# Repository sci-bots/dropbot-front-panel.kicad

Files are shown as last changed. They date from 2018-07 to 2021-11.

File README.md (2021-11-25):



# DropBot v3 front panel

The front panel board provides the power (+3.3V, +12V) and communication (i2c) bus for the other boards in the [DropBot v3 system][dropbot] and routes the high-voltage outputs from the switching boards to the pogo-pin board.

For more information, please visit https://sci-bots.com

[Sci-Bots logo][sci-bots]

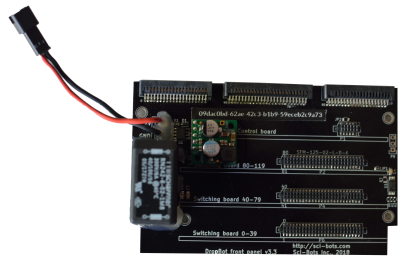
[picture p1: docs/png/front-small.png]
front

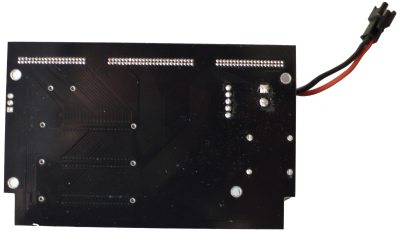
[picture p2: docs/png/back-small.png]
back


This design is open-source hardware released under a [Creative Commons Attribution-ShareAlike licence][cc-by-sa].

[][cc-by-sa]

[dropbot]: https://github.com/sci-bots/dropbot-v3
[sci-bots]: https://sci-bots.com/
[cc-by-sa]: http://creativecommons.org/licenses/by-sa/3.0

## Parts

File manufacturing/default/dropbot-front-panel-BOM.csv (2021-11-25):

Refs | Quantity | MPN | Manufacturer | datasheet | footprint | value
C1-C4 | 4 | CL21B104KBCNNNC | Samsung |  | Capacitors_SMD:C_0805 | 0.1uF
D1 | 1 | MMSZ5240BS-7-F | Diodes Inc. |  | Diodes_SMD:D_SOD-323 | 10V
JP1 | 1 | RC0805JR-070RL | Yageo |  | Resistors_SMD:R_0805 | JUMPER
JP2 | 1 | DNP | DNP |  | Resistors_SMD:R_0805 | JUMPER
JP3 | 1 | DNP | DNP |  | Resistors_SMD:R_0603 | A0
JP4 | 1 | DNP | DNP |  | Resistors_SMD:R_0603 | A1
JP5 | 1 | DNP | DNP |  | Resistors_SMD:R_0603 | A2
L2 | 1 | RN242-6-02-1M8 | Schaffner |  | Sci-Bots:RN242-X-02-XXX | 1.8mH
P1 | 1 | SFM-105-02-L-D-A | Samtec |  | Sci-Bots:SFM-105-02-XXX-D-A | SFM-105-02-L-D-A
P10 | 1 | DNP | DNP |  | Connect:bornier2 | Conn_01x02
P8, P13-P15 | 4 | SFM-125-02-L-D-A | Samtec |  | Connect:1pin | Conn_01x01
P2, P4, P6 | 3 | TFM-120-01-L-D-RA | Samtec |  | Sci-Bots:SFM-125-02-XXX-D-A | SFM-125-02-L-D-A
P3, P7 | 2 | TFM-125-01-L-D-RA | Samtec |  | Sci-Bots:TFM-120-01-XXX-D-RA | TFM-120-01-L-D-RA
P5 | 1 | DNP | DNP |  | Sci-Bots:TFM-125-01-XXX-D-RA | TFM-125-01-L-D-RA
P9 | 1 | DNP | DNP |  | Pin_Headers:Pin_Header_Straight_1x03 | Conn_01x03
Q1 | 1 | IRF9388TRPBF | Infineon |  | Power_Integrations:SO-8 | IRF9388TRPBF
R1, R7 | 2 | RC0805FR-0710KL | Yageo |  | Resistors_SMD:R_0805 | 10k
U1 | 1 | M24C02-DRDW8TP/K | STMicroelectronics |  | Housings_SSOP:TSSOP-8_4.4x3mm_Pitch0.65mm | CAT24C__
U2 | 1 | D24V22F3 | Pololu |  | Sci-Bots:D24V22F | D24V22F3

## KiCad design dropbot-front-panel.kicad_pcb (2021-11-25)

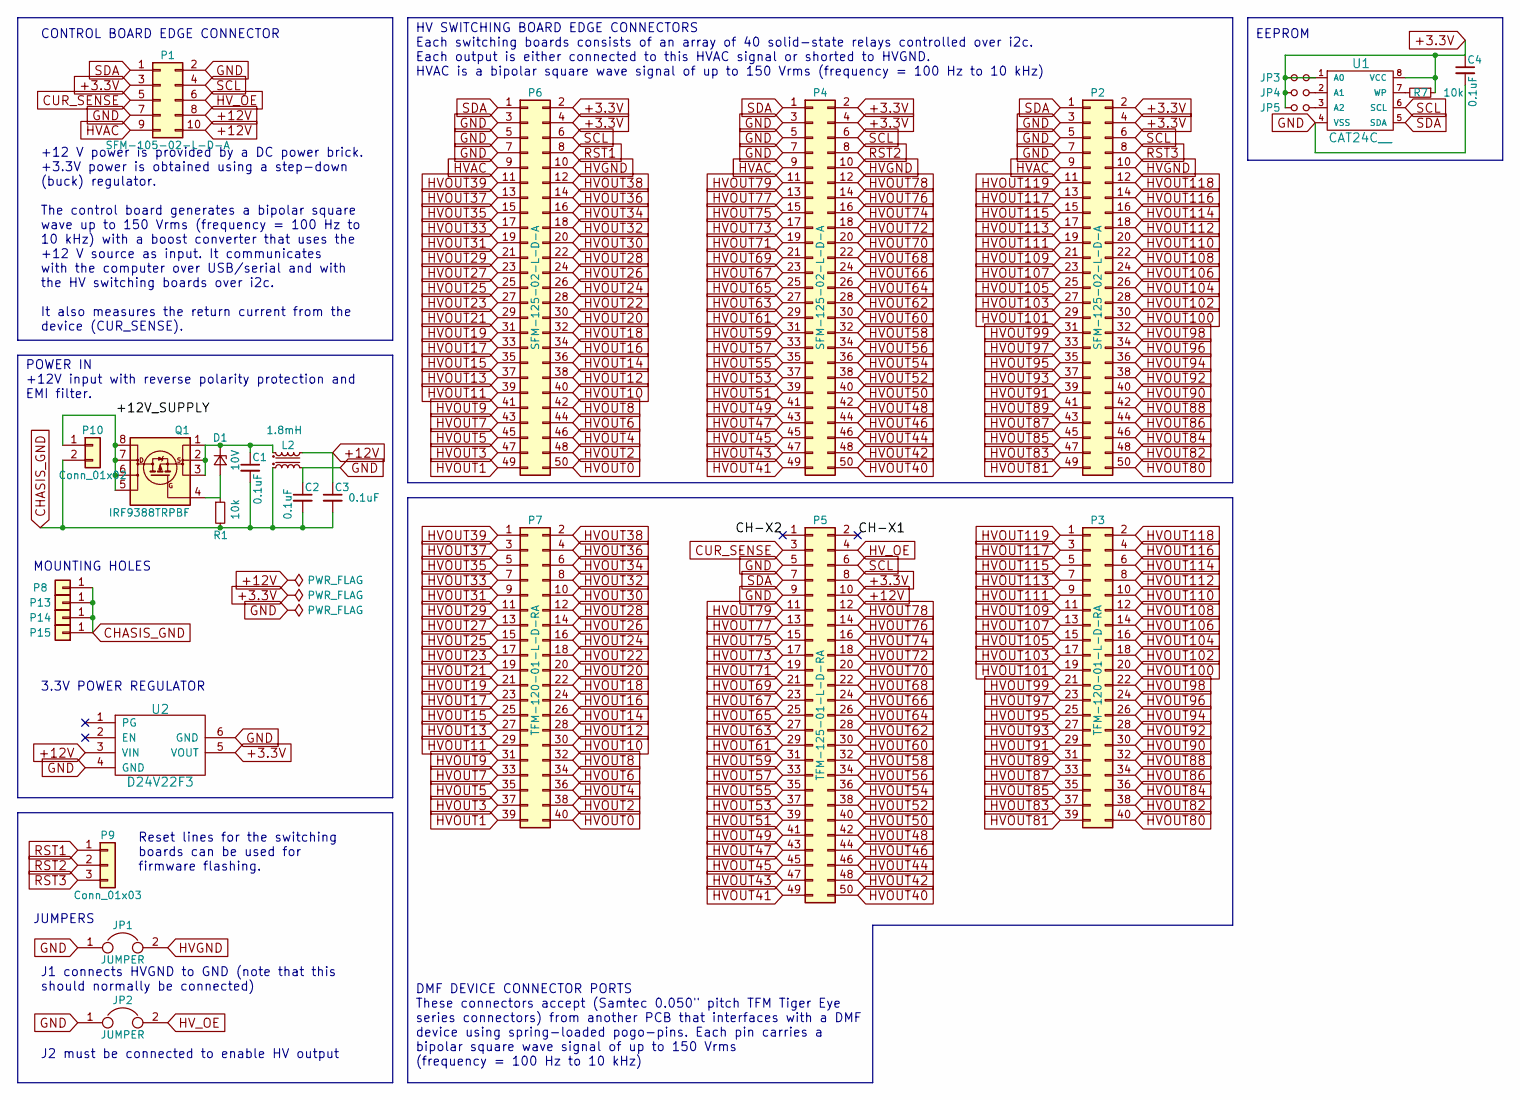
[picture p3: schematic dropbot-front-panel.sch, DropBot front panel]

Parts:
C1, C2, C3, C4: 0.1uF; C_0805; MPN CL21B104KBCNNNC
D1: 10V; D_SOD-323; MPN MMSZ5240BS-7-F
JP1: JUMPER; R_0805; MPN RC0805JR-070RL
JP2: JUMPER; R_0805; MPN DNP
JP3: A0; R_0603; MPN DNP
JP4: A1; R_0603; MPN DNP
JP5: A2; R_0603; MPN DNP
L2: 1.8mH; RN242-X-02-XXX; MPN RN242-6-02-1M8
P1: SFM-105-02-L-D-A; SFM-105-02-XXX-D-A; MPN SFM-105-02-L-D-A
P2, P4, P6: SFM-125-02-L-D-A; SFM-125-02-XXX-D-A; MPN TFM-120-01-L-D-RA
P3, P7: TFM-120-01-L-D-RA; TFM-120-01-XXX-D-RA; MPN TFM-125-01-L-D-RA
P5: TFM-125-01-L-D-RA; TFM-125-01-XXX-D-RA; MPN DNP
P8, P13, P14, P15: Conn_01x01; 1pin; MPN SFM-125-02-L-D-A
P9: Conn_01x03; Pin_Header_Straight_1x03; MPN DNP
P10: Conn_01x02; bornier2; MPN DNP
Q1: IRF9388TRPBF; SO-8; MPN IRF9388TRPBF
R1, R7: 10k; R_0805; MPN RC0805FR-0710KL
U1: CAT24C__; TSSOP-8_4.4x3mm_Pitch0.65mm; MPN M24C02-DRDW8TP/K
U2: D24V22F3; D24V22F; MPN D24V22F3

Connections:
+3.3V: C4.1, JP3.1, JP3.2, JP4.1, JP5.1, P1.3, P2.2, P2.4, P4.2, P4.4, P5.8, P6.2, P6.4, R7.1, U1.1 (A0), U1.8 (VCC), U2.5 (VOUT)
+12V: C3.1, L2.2, P1.8, P1.10, P5.10, U2.3 (VIN)
/+12V_SUPPLY: P10.1, Q1.5 (D), Q1.6 (D), Q1.7 (D), Q1.8 (D)
/CH-X1: P5.2
/CH-X2: P5.1
CHASIS_GND: C1.2, C2.2, C3.2, L2.4, P8.1, P10.2, P13.1, P14.1, P15.1, R1.2
CUR_SENSE: P1.5, P5.3
GND: C2.1, C4.2, JP1.1, JP2.1, L2.3, P1.2, P1.7, P2.3, P2.5, P2.7, P4.3, P4.5, P4.7, P5.5, P5.9, P6.3, P6.5, P6.7, U1.4 (VSS), U2.4 (GND), U2.6 (GND)
HVAC: P1.9, P2.9, P4.9, P6.9
HVGND: JP1.2, P2.10, P4.10, P6.10
HVOUT0: P6.50, P7.40
HVOUT1: P6.49, P7.39
HVOUT2: P6.48, P7.38
HVOUT3: P6.47, P7.37
HVOUT4: P6.46, P7.36
HVOUT5: P6.45, P7.35
HVOUT6: P6.44, P7.34
HVOUT7: P6.43, P7.33
HVOUT8: P6.42, P7.32
HVOUT9: P6.41, P7.31
HVOUT10: P6.40, P7.30
HVOUT11: P6.39, P7.29
HVOUT12: P6.38, P7.28
HVOUT13: P6.37, P7.27
HVOUT14: P6.36, P7.26
HVOUT15: P6.35, P7.25
HVOUT16: P6.34, P7.24
HVOUT17: P6.33, P7.23
HVOUT18: P6.32, P7.22
HVOUT19: P6.31, P7.21
HVOUT20: P6.30, P7.20
HVOUT21: P6.29, P7.19
HVOUT22: P6.28, P7.18
HVOUT23: P6.27, P7.17
HVOUT24: P6.26, P7.16
HVOUT25: P6.25, P7.15
HVOUT26: P6.24, P7.14
HVOUT27: P6.23, P7.13
HVOUT28: P6.22, P7.12
HVOUT29: P6.21, P7.11
HVOUT30: P6.20, P7.10
HVOUT31: P6.19, P7.9
HVOUT32: P6.18, P7.8
HVOUT33: P6.17, P7.7
HVOUT34: P6.16, P7.6
HVOUT35: P6.15, P7.5
HVOUT36: P6.14, P7.4
HVOUT37: P6.13, P7.3
HVOUT38: P6.12, P7.2
HVOUT39: P6.11, P7.1
HVOUT40: P4.50, P5.50
HVOUT41: P4.49, P5.49
HVOUT42: P4.48, P5.48
HVOUT43: P4.47, P5.47
HVOUT44: P4.46, P5.46
HVOUT45: P4.45, P5.45
HVOUT46: P4.44, P5.44
HVOUT47: P4.43, P5.43
HVOUT48: P4.42, P5.42
HVOUT49: P4.41, P5.41
HVOUT50: P4.40, P5.40
HVOUT51: P4.39, P5.39
HVOUT52: P4.38, P5.38
HVOUT53: P4.37, P5.37
HVOUT54: P4.36, P5.36
HVOUT55: P4.35, P5.35
HVOUT56: P4.34, P5.34
HVOUT57: P4.33, P5.33
HVOUT58: P4.32, P5.32
HVOUT59: P4.31, P5.31
HVOUT60: P4.30, P5.30
HVOUT61: P4.29, P5.29
HVOUT62: P4.28, P5.28
HVOUT63: P4.27, P5.27
HVOUT64: P4.26, P5.26
HVOUT65: P4.25, P5.25
HVOUT66: P4.24, P5.24
HVOUT67: P4.23, P5.23
HVOUT68: P4.22, P5.22
HVOUT69: P4.21, P5.21
HVOUT70: P4.20, P5.20
HVOUT71: P4.19, P5.19
HVOUT72: P4.18, P5.18
HVOUT73: P4.17, P5.17
HVOUT74: P4.16, P5.16
HVOUT75: P4.15, P5.15
HVOUT76: P4.14, P5.14
HVOUT77: P4.13, P5.13
HVOUT78: P4.12, P5.12
HVOUT79: P4.11, P5.11
HVOUT80: P2.50, P3.40
HVOUT81: P2.49, P3.39
HVOUT82: P2.48, P3.38
HVOUT83: P2.47, P3.37
HVOUT84: P2.46, P3.36
HVOUT85: P2.45, P3.35
HVOUT86: P2.44, P3.34
HVOUT87: P2.43, P3.33
HVOUT88: P2.42, P3.32
HVOUT89: P2.41, P3.31
HVOUT90: P2.40, P3.30
HVOUT91: P2.39, P3.29
HVOUT92: P2.38, P3.28
HVOUT93: P2.37, P3.27
HVOUT94: P2.36, P3.26
HVOUT95: P2.35, P3.25
HVOUT96: P2.34, P3.24
HVOUT97: P2.33, P3.23
HVOUT98: P2.32, P3.22
HVOUT99: P2.31, P3.21
HVOUT100: P2.30, P3.20
HVOUT101: P2.29, P3.19
HVOUT102: P2.28, P3.18
HVOUT103: P2.27, P3.17
HVOUT104: P2.26, P3.16
HVOUT105: P2.25, P3.15
HVOUT106: P2.24, P3.14
HVOUT107: P2.23, P3.13
HVOUT108: P2.22, P3.12
HVOUT109: P2.21, P3.11
HVOUT110: P2.20, P3.10
HVOUT111: P2.19, P3.9
HVOUT112: P2.18, P3.8
HVOUT113: P2.17, P3.7
HVOUT114: P2.16, P3.6
HVOUT115: P2.15, P3.5
HVOUT116: P2.14, P3.4
HVOUT117: P2.13, P3.3
HVOUT118: P2.12, P3.2
HVOUT119: P2.11, P3.1
HV_OE: JP2.2, P1.6, P5.4
unnamed: C1.1, D1.1 (K), L2.1, Q1.1 (S), Q1.2 (S), Q1.3 (S)
unnamed: D1.2 (A), Q1.4 (G), R1.1
unnamed: JP4.2, U1.2 (A1)
unnamed: JP5.2, U1.3 (A2)
unnamed: R7.2, U1.7 (WP)
RST1: P6.8, P9.1
RST2: P4.8, P9.2
RST3: P2.8, P9.3
SCL: P1.4, P2.6, P4.6, P5.6, P6.6, U1.6 (SCL)
SDA: P1.1, P2.1, P4.1, P5.7, P6.1, U1.5 (SDA)

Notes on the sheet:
CONTROL BOARD EDGE CONNECTOR
HV SWITCHING BOARD EDGE CONNECTORS Each switching boards consists of an array of 40 solid-state relays controlled over i2c. Each output is either connected to this HVAC signal or shorted to HVGND. HVAC is a bipolar square wave signal of up to 150 Vrms (frequency = 100 Hz to 10 kHz)
DMF DEVICE CONNECTOR PORTS These connectors accept (Samtec 0.050" pitch TFM Tiger Eye series connectors) from another PCB that interfaces with a DMF device using spring-loaded pogo-pins. Each pin carries a bipolar square wave signal of up to 150 Vrms (frequency = 100 Hz to 10 kHz)
JUMPERS
J1 connects HVGND to GND (note that this should normally be connected)
J2 must be connected to enable HV output
+12 V power is provided by a DC power brick. +3.3V power is obtained using a step-down (buck) regulator. The control board generates a bipolar square wave up to 150 Vrms (frequency = 100 Hz to 10 kHz) with a boost converter that uses the +12 V source as input. It communicates with the computer over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
Reset lines for the switching boards can be used for firmware flashing.
3.3V POWER REGULATOR
POWER IN +12V input with reverse polarity protection and EMI filter.
MOUNTING HOLES
EEPROM

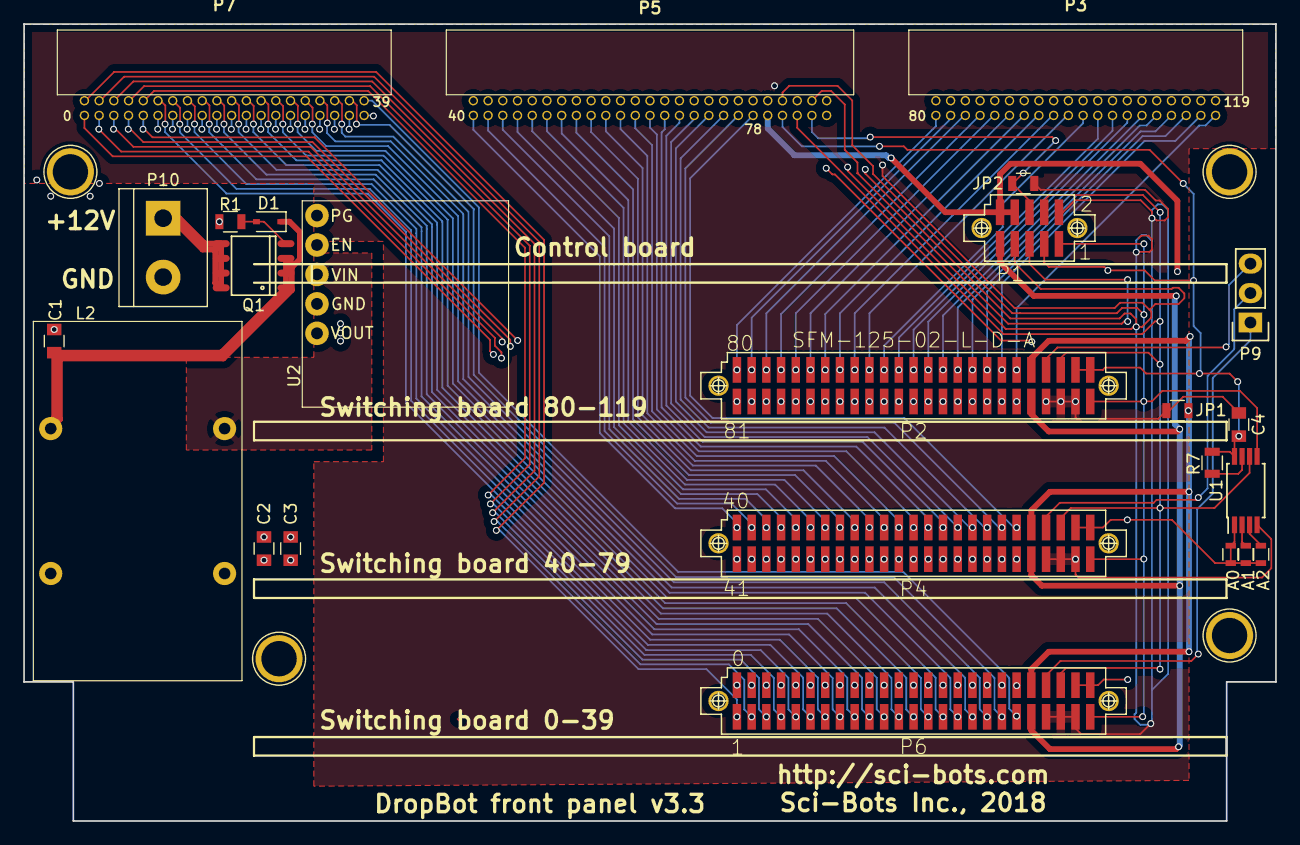
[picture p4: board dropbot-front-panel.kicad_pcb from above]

Board: 4 copper layers, 108.0 x 68.8 mm, 29 parts (0 on the bottom side), 139 nets.

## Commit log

2016-12-19 Update documentation on schematic and add pdf output
    [dropbot-front-pannel-B.Cu.gbr, dropbot-front-pannel-B.Mask.gbr, dropbot-front-pannel-B.Paste.gbr, dropbot-front-pannel-B.SilkS.gbr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]
2016-12-19 Remove control board pcb layout from repo
    [dropbot_control_board.kicad_pcb]
2017-01-05 Update BOM
    [dropbot-front-pannel.sch, dropbot-front-pannel_BOM.csv]
2017-01-09 Fix BOM
    [dropbot-front-pannel.sch, dropbot-front-pannel_BOM.csv]
2017-03-01 [WIP] Update PCB to use Samtec connectors
    Update PCB to use Samtec connectors instead of PCB edge connections.
    This is because the edge connector slots are not rated for high-voltage
    (i.e., they are not rated for over 30V).
    [dropbot-front-pannel.kicad_pcb, dropbot-front-pannel.sch]
2017-03-01 Add PCB cut-aways for box stand-offs
    [dropbot-front-pannel.kicad_pcb]
2017-03-01 Increase height of PCB to match dims of box
    [dropbot-front-pannel.kicad_pcb]
2017-03-02 [WIP] Update to use new Samtec connectors...
    * add USB passthrough
    * add 3.3V power regulator
    * add reverse polarity protection on +12V power line
    [dropbot-front-pannel.kicad_pcb, dropbot-front-pannel.sch]
2017-03-03 [WIP] update USB parts, replace jumpers with 0805 pads
    [dropbot-front-pannel.kicad_pcb, dropbot-front-pannel.sch]
2017-03-05 Add switching/control board outlines
    [dropbot-front-pannel.kicad_pcb]
2017-03-07 [WIP] Add EMI suppression, ESD protection
    [dropbot-front-pannel-B.Cu.gbr, dropbot-front-pannel-B.Fab.gbr, dropbot-front-pannel-B.Mask.gbr, dropbot-front-pannel-B.Paste.gbr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]
2017-03-08 [WIP] route HV outputs
    [dropbot-front-pannel-B.Cu.gbr, dropbot-front-pannel-B.Fab.gbr, dropbot-front-pannel-B.Mask.gbr, dropbot-front-pannel-B.Paste.gbr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]
2017-03-08 [WIP] swap order of switching boards
    [dropbot-front-pannel.kicad_pcb, dropbot-front-pannel.sch]
2017-03-08 [WIP] route power, ground planes
    [dropbot-front-pannel.kicad_pcb, dropbot-front-pannel.sch]
2017-03-09 Finish routing all nets, move components to front of board
    [dropbot-front-pannel-B.Cu.gbr, dropbot-front-pannel-B.Fab.gbr, dropbot-front-pannel-B.Mask.gbr, dropbot-front-pannel-B.Paste.gbr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]
2017-03-09 Fix control board connector to match v3.1
    [dropbot-front-pannel-B.Cu.gbr, dropbot-front-pannel-B.Fab.gbr, dropbot-front-pannel-B.Mask.gbr, dropbot-front-pannel-B.Paste.gbr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]
2017-03-22 Remove usb passthrough, fix SMT connector...
    * remove usb passthrough
    * fix SMT connector footprints (missing holes)
    * remove USB passthrough (now on control board)
    * move power connector to top of board
    * increase height of cutouts in bottom corners
    [dropbot-front-pannel-B.Cu.gbr, dropbot-front-pannel-B.Fab.gbr, dropbot-front-pannel-B.Mask.gbr, dropbot-front-pannel-B.Paste.gbr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]
2017-04-20 Fix part numbers for P3 and P7
    [dropbot-front-pannel.sch, dropbot-front-pannel_BOM.csv]
2017-04-25 label +12V and G on power connector
    [dropbot-front-pannel.kicad_pcb]
2017-04-28 Fix spelling mistake (pannel -> panel)
    [dropbot-front-panel-B.Cu.gbr, dropbot-front-panel-B.Fab.gbr, dropbot-front-panel-B.Mask.gbr, dropbot-front-panel-B.Paste.gbr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]
2017-09-19 Fix #1, #2 and #3
    1. Add i2c EEPROM chip to store serial number, hardware version, etc.
    2. Move C2 and C3 (they currently collide with the 2nd switching board)
    3. Fix reverse polarity protection
    [dropbot-front-panel-B.Cu.gbr, dropbot-front-panel-B.Fab.gbr, dropbot-front-panel-B.Mask.gbr, dropbot-front-panel-B.Paste.gbr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]
2017-09-19 Remove extraneous gerber files
    [dropbot-front-pannel-B.Cu.gbr, dropbot-front-pannel-B.Fab.gbr, dropbot-front-pannel-B.Mask.gbr, dropbot-front-pannel-B.Paste.gbr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]
2018-03-09 Update to use Sci-Bots library
    [dropbot-front-panel.kicad_pcb, dropbot-front-panel.sch, dropbot-front-panel_BOM.csv]
2018-03-15 Use through-hole connectors to pogo-pin board
    [dropbot-front-panel-B.Cu.gbr, dropbot-front-panel-B.Fab.gbr, dropbot-front-panel-B.Mask.gbr, dropbot-front-panel-B.Paste.gbr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]
2018-06-08 Update routing of TFM connectors, replace eeprom part
    Fixes #4
    [dropbot-front-panel-B.Cu.gbr, dropbot-front-panel-B.Fab.gbr, dropbot-front-panel-B.Mask.gbr, dropbot-front-panel-B.Paste.gbr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]
2021-11-08 Reorganize folder
    [dropbot-front-panel-B.Cu.gbr, dropbot-front-panel-B.Fab.gbr, dropbot-front-panel-B.Mask.gbr, dropbot-front-panel-B.Paste.gbr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]
2021-11-09 Update to kicad 5
    [dropbot-front-panel.sch]
2021-11-09 Add manufacturing folder
    [dropbot-front-panel-BOM.csv, dropbot-front-panel-NPTH.drl, dropbot-front-panel.drl, dropbot-front-panel.gbl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]
2021-11-25 Update netlist
    [dropbot-front-panel.kicad_pcb]
2021-11-25 Fix ERC errors
    [dropbot-front-panel.kicad_pcb, dropbot-front-panel.sch]
2021-11-25 Add filters for DRC
